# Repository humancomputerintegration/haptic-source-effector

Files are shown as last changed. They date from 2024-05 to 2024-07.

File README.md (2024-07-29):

# Haptic Source-Effector: Full-Body Haptics via Non-Invasive Brain Stimulation

This is the repository for hardware and codes used for the "Haptic Source-Effector: Full-Body Haptics via Non-Invasive Brain Stimulation" paper (ACM CHI2024).

For more information, please refer to our paper: http://lab.plopes.org/#source-effector

## citing
When using or building upon this device in an academic publication, please consider citing as follows:

Yudai Tanaka, Jacob Serfaty, and Pedro Lopes. 2024. Haptic Source-Effector: Full-Body Haptics via Non-Invasive Brain Stimulation. In Proceedings of the 2024 CHI Conference on Human Factors in Computing Systems (CHI'24), May 11-16, 2024, Hawaii, USA. ACM, NewYork, NY, USA, 15 pages. [https://dl.acm.org/doi/abs/10.1145/3544548.3581382](https://dl.acm.org/doi/full/10.1145/3613904.3642483)

## contact
For any questions about this repository, please contact yudaitanaka@uchicago.edu and/or jserfaty@uchicago.edu

## Hardware
Our device is designed to be directly affixed to Meta Quest 2 and its Elite Strap.

coilMount.stl, servoBoard.stl, and servoToHeadset(needx2).stl are for 3D-printed parts we use to incorporate the coil and the servo motor into our device.

We also use custom-cut 3-mm aluminum plates as the device's mechanical joints. The railJoints.ai has the cut patterns.

partsList.xlsx covers all the other components you need to build our device.

## Codes/motorControl
Codes to control the motors on the source-effector device.

this is on Unity2020.3.21f1. you might need the same version.

this application may only work on Mac computers.

PREP  
direct to "Assets/Scenes/SampleScene". that's the scene.

this one controls the motors via Serial and receives commands from the Windows VR PC (connected to Quest) over OSC,
hence you have to configure the two things respectively.

1: go to the stimTest script attached to tmsMotors game object. check the serial ports for the servo and the linear (their usb-c cables are labeled) and change "serialportServo" (line64) and "serialportLinear" (line78) accordingly.

2: if you don't do VR, you can skip this part. go to the OSC game object and make sure "In Port" is the same four digits as the ones on "Out Port" of the OSC script attached to the Controller GameObject in the Unity VR application. ask Jacob if you have any questions re: the Windows PC.

RUN  
after the above configuration is done, make sure that you can receive Serial messages from both the servo and linear via Arduino serial monitor. the Serial doesn't work even the ports are configured unless you open the Serial monitors beforehand.  

now you can control the motors on stimTest at inspector.

Calibration/Registration:  
make sure the calibration toggle is ON. in this state, you can move the motors by moving the three sliders on the inspector. you can register 6 different sets of the motor values as target positions: ORIGIN; Left Foot; Right Foot; Left Hand; Right Hand; and Jaw.

first, you adjust the motor positions via the sliders once you found a good position, you can click the Calib State tab and choose a target that you want to register these motor values for. if the registration is successful, these motor values will be shown next to the labels of the targets.

Move to the targets:  
now, toggle the calibration bool to OFF. in this state, you can move the motors to the registered target positions. to do so, you can simply click the State tab and select the target.
if you want to update the target positions, go back to the calibration state by toggling the bool and repeat the calibration procedure.

## Codes/Arduino
Firmware for the microcontrollers to control the motors. Upload "coilPositionControlX.ino" and "coilPositionControlYZ.ino" to each Seeeduino XIAO.

## Codes/TMS
Codes to control the TMS stimulator. Run tms.py while the Magstim device is connected to your PC/laptop's serial port.

## Codes/VR
Codes to run our interactive VR game.

this is on Unity2020.3.8f1. you might need the same version.

running this VR game requires 3 total applications: 
1. this VR scene
2. the tms.py application from Codes/TMS on the computer attached to the TMS coil
3. the Codes/motorControl application on a Mac computer attached to the motor mechanism for our device.

PREP  
direct to "Assets/Scenes/Testing". that's the main game scene. alternatively, direct to "Assets/Scenes/Calibration" for the same calibration process as in the Codes/MotorControl Unity project.

this VR scene requires SteamVR hand and foot tracking using HTC Vive trackers and our hardware device which performs tracking with a Meta Quest 2. pair the Meta Quest 2 to the PC using SteamVR with Quest Link (ideally AirLink with the AirLink).

to unify base station tracking for the HTC Vive trackers and Meta Quest 2 inside-out tracking, use the program [OpenVR Space Calibrator](https://github.com/pushrax/OpenVR-SpaceCalibrator). we recommend performing the calibration for OpenVR Space Calibrator by only pairing one HTC Vive tracker, holding it next to the Meta Quest 2 headset, initiating fast calibration, and looking around in every direction. the remaining HTC Vive trackers can be paired after calibration is complete.

when pairing the HTC Vive trackers, attach 4 trackers to the body: one on each hand and one on each foot. in SteamVR, assign the left hand tracker to "Left Shoulder", the right hand tracker to "Right Hand", the left foot tracker to "Left Foot", and the right foot tracker to "Right Foot".

before running:
1. connect all computers to the same WiFi network
2. make sure the "Out IP" on the OSC script attached to the Controller GameObject in Unity is set to the IP address of the computer that controls the TMS coil's movements
3. skip this step if the TMS coil is attached to the same PC that is running the VR application (which we recommend). make sure the "Out IP" on the TMS Controller GameObject (which is a child object of the Controller GameObject) in Unity is set to the IP address of the computer that is connected to the TMS coil.

RUN  
after the above configuration is done, first run Codes/motorControl on a separate Mac computer as described above. then, on the PC connected to the TMS coil, run tms.py. finally, once tms.py is properly initiated, run the Unity VR scene.

if the Unity VR scene is stopped, an emergency stop signal will be sent to the tms.py script that prevents further TMS stimulations. 

to restart the VR application after it is stopped, make sure to stop and restart tms.py. if it is still running, you do not need to restart the Codes/motorControl application.

PLAYING THE GAME  
shoot blasts by placing one hand outwards towards the enemy, grabbing the wrist of that hand with the opposite hand, and waiting for the blast to charge up and fire. 

while charging attacks, the enemy may fire its own attacks at the hands and feet.

ammo is listed on the back of each hand. when ammo reaches 0, an ammo box may fall. step on the box with the foot closest to the box to break it and receive ammo.

after defeating 3 enemies, a button will spawn. press the button with the right hand to finish the game.

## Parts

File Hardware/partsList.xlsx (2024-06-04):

name | pcs | link
Shafts
Linear Motion Shaft D8x496mm | 2 | https://www.studica.com/studica-robotics-brand/linear-motion-shaft-d8x496mm-h
Linear Motion Shaft D8x300mm | 2 | https://www.mcmaster.com/4316N112/
Linear Motion Shaft D6x150mm | 2 | https://www.mcmaster.com/4316N103/
4x56mm Shaft | 2 | https://www.robots4all.be/D-As-4x56-mm-(4-stuks)?Product=133090511&Lng=en
4mm Shaft collar | 12 | https://www.mcmaster.com/6056N12/
Brackets
Makeblock Bracket 3x3 | 2 | https://macrotronics.net/makeblock-bracket-3x3-blue-pack-61500-p-38329.html
Makeblock Bracket U1 | 2 | https://www.ebay.com/itm/324275754090
Bearings
Linear Motion Slide Unit 8mm | 6 | https://www.studica.com/makeblock/makeblock-linear-motion-slide-unit-8mm-pair-
Linear Motion Slide Unit 6mm | 2 | https://www.mcmaster.com/9338T67/
Rotation bearing | 2 | https://www.mcmaster.com/8600N9/
Rotation bearing for the front | 1 | https://www.mcmaster.com/4575N23/
Rotation axis for the front | 1 | https://www.mcmaster.com/91125A432/
Screws
M4x8 Screw | 30 | https://www.mcmaster.com/92095A189/
M4x16 Screw | 10 | https://www.mcmaster.com/92095A194/
M4x22 Screw | 10 | https://www.mcmaster.com/92095A479/
M3 Screw | 20 | https://www.mcmaster.com/92095A181/
4-40x1/4 Screw for the front | 1 | https://www.mcmaster.com/92949A106/
Nuts
M4 Nut | 10 | https://www.mcmaster.com/91828A231/
M3 Nut | 20 | https://www.mcmaster.com/90592A085/
Spacers
M3x15 threaded spacer | 4 | https://www.amazon.com/dp/B06Y5TJXY1/
M4x2 spacer | 4 | https://www.mcmaster.com/92871A002/
M3x2 mm spacer | 4 | https://www.mcmaster.com/92871A102/
Motors
X servo motor | 1 | https://www.pololu.com/product/3429
Y linear actuator | 1 | https://www.actuonix.com/p8-75-165-12-p
Z linear actuator | 1 | https://www.actuonix.com/l16-100-63-12-p
Microcontroller
Seeeduino XIAO | 2 | https://www.seeedstudio.com/Seeeduino-XIAO-Arduino-Microcontroller-SAMD21-Cortex-M0+-p-4426.html
Encoders
Linear actuator encoders | 2 | https://www.adafruit.com/product/3190

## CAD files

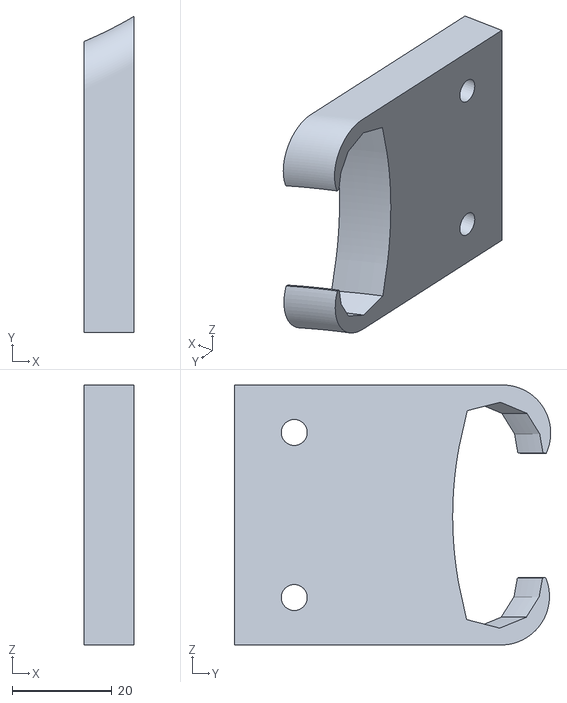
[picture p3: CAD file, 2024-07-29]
Hardware/servoToHeadset(needx2).stl
10.0 x 63.3 x 52.0

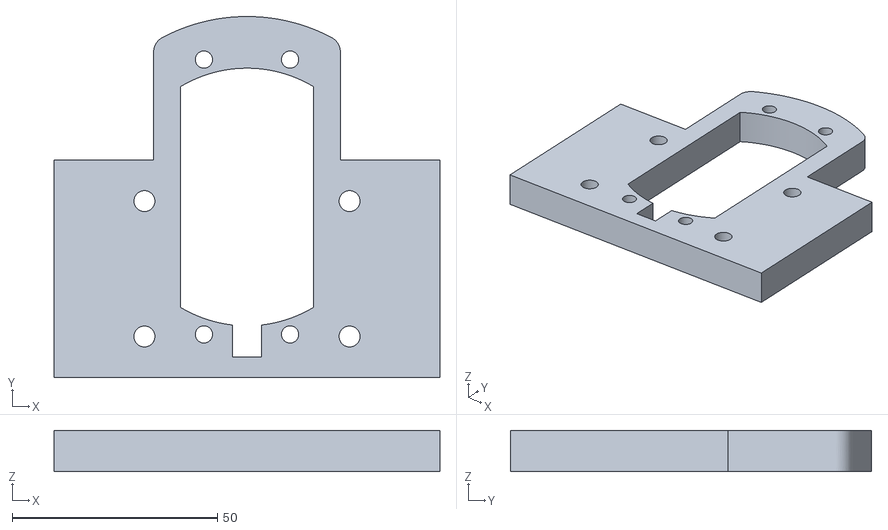
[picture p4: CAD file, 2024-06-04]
Hardware/servoBoard.stl
94.0 x 88.0 x 10.0

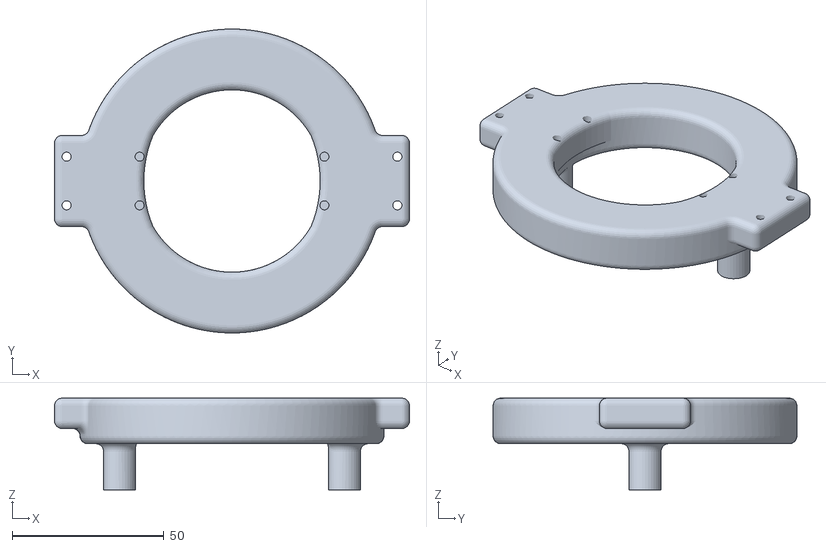
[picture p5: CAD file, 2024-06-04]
Hardware/coilMount.stl
116.8 x 100.0 x 30.2

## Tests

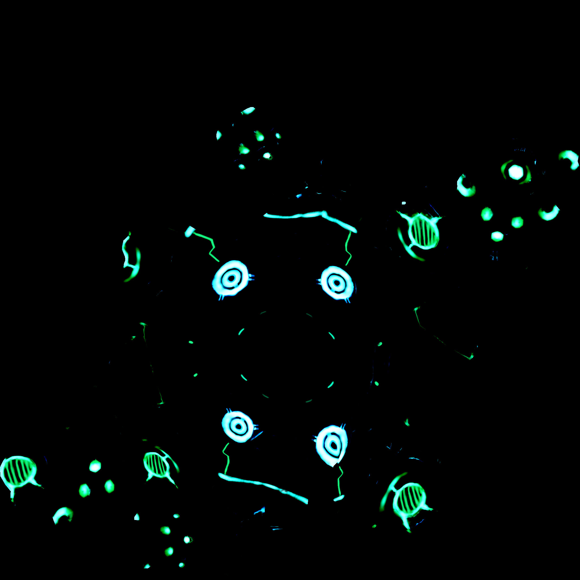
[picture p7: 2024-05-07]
Codes/VR/TMS VR SteamVR [Testing]/Assets/Laser/Reaper MachineGun/Demoscene/Resources/Sci-Fi/Platform/Textures/platform_emisive.jpg

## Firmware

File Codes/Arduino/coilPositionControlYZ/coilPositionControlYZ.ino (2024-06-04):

#define L1_1 3
#define L1_2 4
#define L2_1 5
#define L2_2 6

String mes2, mes3;

int targetValueL1, targetValueL2;
int errorMarginL = 10;

void setup() {
  Serial.begin(115200);
  while (!Serial);
  pinMode(L1_1, OUTPUT);
  pinMode(L1_2, OUTPUT);
  targetValueL1=targetValueL2=500;
}

void loop() {
  if (Serial.available()) {
    mes2 = Serial.readStringUntil(',');
    mes3 = Serial.readStringUntil('\n');
    
    targetValueL1 = mes2.toInt();
    targetValueL2 = mes3.toInt();

    delay(1);
  }

  // Logic for L1
  int sensorValueL1 = analogRead(A2);
  controlMotor(sensorValueL1, targetValueL1, 1);

  // Logic for L2
  int sensorValueL2 = analogRead(A1);  // Assuming the sensor for M2 is on A11
  controlMotor(sensorValueL2, targetValueL2, 2);

  Serial.print("M1: ");
  Serial.print(sensorValueL1);
  Serial.print(", M2: ");
  Serial.println(sensorValueL2);
  delay(1);
}

void controlMotor(int sensorValue, int targetValue, int motorNum) {
  if (abs(sensorValue - targetValue) < errorMarginL) {
    if (motorNum == 1) {
      analogWrite(L1_1, 0);
      digitalWrite(L1_1, LOW);
      analogWrite(L1_2, 0);
    } else {
      analogWrite(L2_1, 0);
      digitalWrite(L2_1, LOW);
      analogWrite(L2_2, 0);
    }
  } 
  else if (sensorValue <= targetValue - 4*errorMarginL) {
    if (motorNum == 1) {
      analogWrite(L1_1, 0);
      digitalWrite(L1_1, LOW);
      analogWrite(L1_2, 200);
    } else {
      analogWrite(L2_1, 0);
      digitalWrite(L2_1, LOW);
      analogWrite(L2_2, 200);
    }
  } 
  else if (sensorValue >= targetValue + 4*errorMarginL) {
    if (motorNum == 1) {
      analogWrite(L1_2, 0);
      digitalWrite(L1_2, LOW);
      analogWrite(L1_1, 200);
    } else {
      analogWrite(L2_2, 0);
      digitalWrite(L2_2, LOW);
      analogWrite(L2_1, 200);
    }
  }
}

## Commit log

2024-06-04 organized the folder structure
    [coilMount.stl, partsList.xlsx, servoBoard.stl, servoToHeadset(needx2).stl]
2024-07-29 hardware revision
    corrected the version for the servoToHeadset hardware component
    [servoToHeadset(needx2).stl]
2024-07-31 added L shape brackets to hardware
    [servoCornerBrackets(needx4).stl]
